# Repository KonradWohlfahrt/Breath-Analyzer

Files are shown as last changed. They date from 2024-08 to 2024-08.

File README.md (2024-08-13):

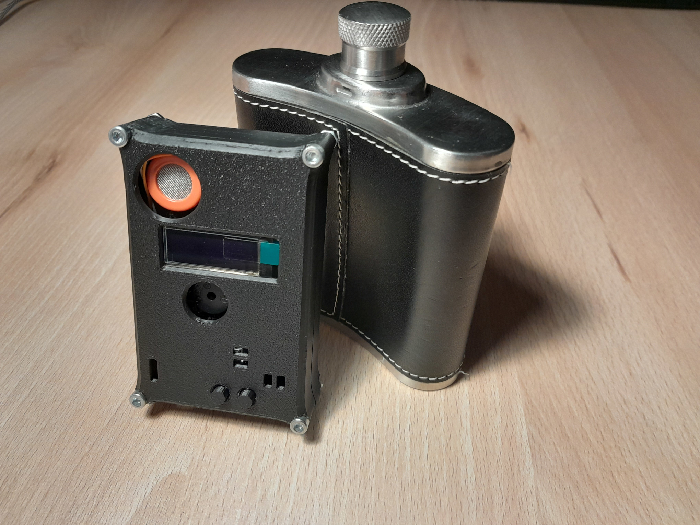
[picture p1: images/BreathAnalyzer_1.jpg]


# DIY BREATH ANALYZER
In this repository you'll find the files for my DIY Breath Analyzer based on the MQ3 Sensor.
Check out my step-by-step guide on [Instructables](https://www.instructables.com/DIY-Breath-Analyzer-With-the-MQ3/).<br>
**NOTE:** This device may not have good accuracy and should not be used as a way to determine your blood alcohol concentration. Refer to commercial products instead! Furthermore, this project was sponsored by [PCBWay](https://www.pcbway.com/). They were so kind to produce the circuit board for this project. PCBWay offers different services, such as pcb fabrication. 
It was the first time for me to use their service. With the gerber files the process of ordering was simple and fast. The quality of the pcbs is awesome! Prefect to bring your diy project to the next level!
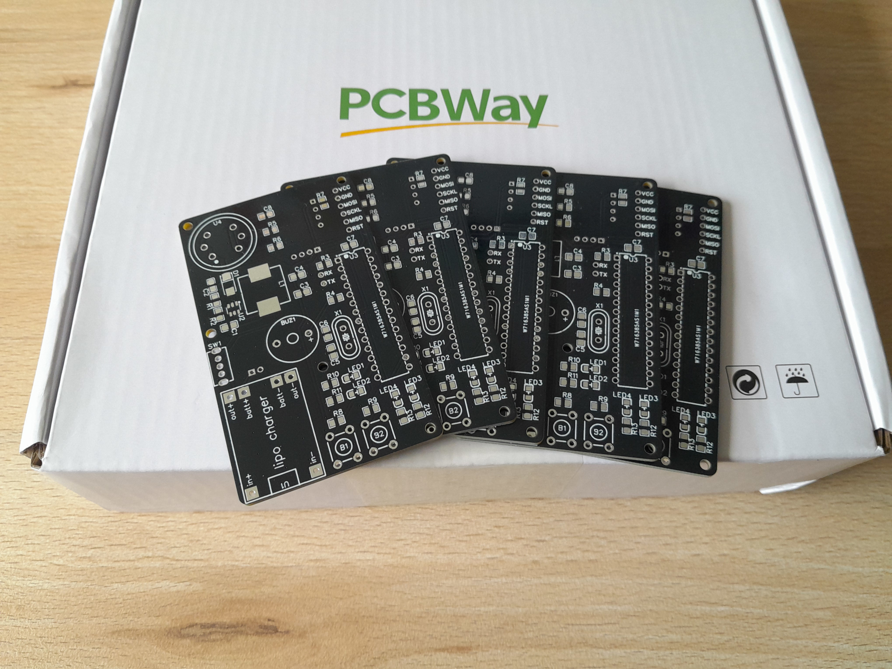
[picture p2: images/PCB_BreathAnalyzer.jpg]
PCBs


***
# BUILDING

**Materials:**<br>
| Component | Amount | Silkscreen label |
|:----------|:------:|-----------------:|
| custom pcb | 1 | - |
| 3D printed case | 1 | - |
| 0.91 I2C OLED display | 1 | - |
| lipo battery | 1 | U6 |
| 2 Pin PH2.0 socket (optional) | 1 | U6 |
| TP4056 charging module | 1 | U1 |
| MT3608 | 1 | U2 |
| ATmega328P + socket (optional) | 1 | U3 |
| MQ3 | 1 | U4 |
| DHT11 | 1 | U5 |
| 16 MHz crystal oscillator | 1 | X1 |
| Piezo buzzer | 1 | BUZ1 |
| Push button 6x6 | 2 | B1,B2 |
| SK12D07VG6 | 1 | SW1 |
| 22uH | 1 | L1 |
| SS34 | 1 | D1 |
| LED 0805 red | 2 | LED1,LED4 |
| LED 0805 green | 1 | LED3 |
| LED 0805 (free color choice) | 1 | LED2 |
| 22uF 0805 | 2 | C1,C2 |
| 10uF 0805 | 1 | C3 |
| 1uF 0805 | 1 | C4 |
| 22pF 0805 | 2 | C5,C6 |
| 100nF 0805 | 2 | C7,C8 |
| 220k 0805 | 1 | R1 |
| 30k 0805 | 1 | R2 |
| 10k 0805 | 4 | R3,R7-R9 |
| 220r 0805 (optional, connect with solder instead) | 1 | R4 |
| 5.1r or 10r 0805 | 1 | R5 |
| 4.7k 0805 | 1 | R6 |
| 1k 0805 | 4 | R10-R13 |
| M2.5x12mm screw + nut | 4 | - |
| M3x20mm screw + nut | 4 | - |

**Soldering:**<br>
Begin to solder the boost converter (U2,D1,L1,C1,C2,R1,R2) and confirm the output voltage of roughly 5V.
Now you can proceed to solder the smd components first and through-hole components second.
You may want to [change](https://www.youtube.com/watch?v=6asCEBm4ZAw) the charge programming resistor of the TP4056 module. Add pins to VCC,GND,MOSI,SCKL,MISO,RST to flash the ATmega. You do not need pins on rx and tx.
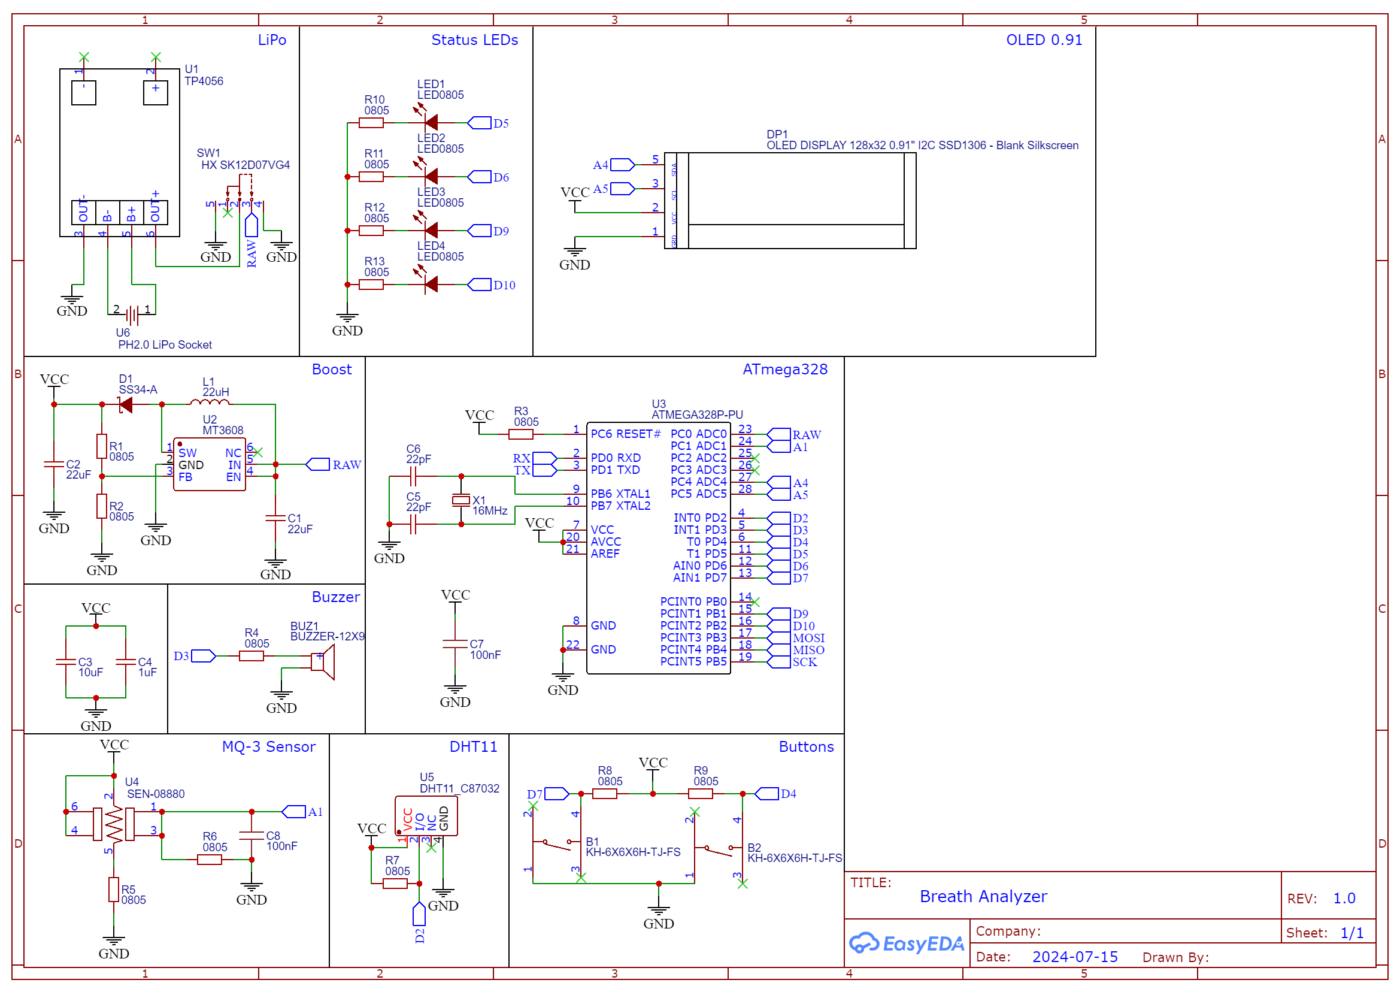
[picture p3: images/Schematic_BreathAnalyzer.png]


***
# Programming and Testing
Heating the sensor once for (over) 24 hours is sufficient to get stable readings. If you leave the device powered off for too long, you should repeat this step.
Install the `MiniCore` board manager, `U8g2`, `DHT` library and upload the test code via an Arduino Uno with `Arduino As ISP`.  Press the buttons to toggle between values: analog value; voltage; sensor resistance; bac in per mille (note: calculate r0 for your sensor first); temperature and humidity.
Flash `BreathAnalyzer.ino` on the Atmega if everything worked as expected and unplug all cables. After plugging in the battery and turning on the device, it should heat up for 30 seconds. Navigate to settings and start to calibrate the device (expose the sensor to clean air only). 
Print the case with the two buttons and screw everything in place. Now your DIY Breath Analyzer is all set up!
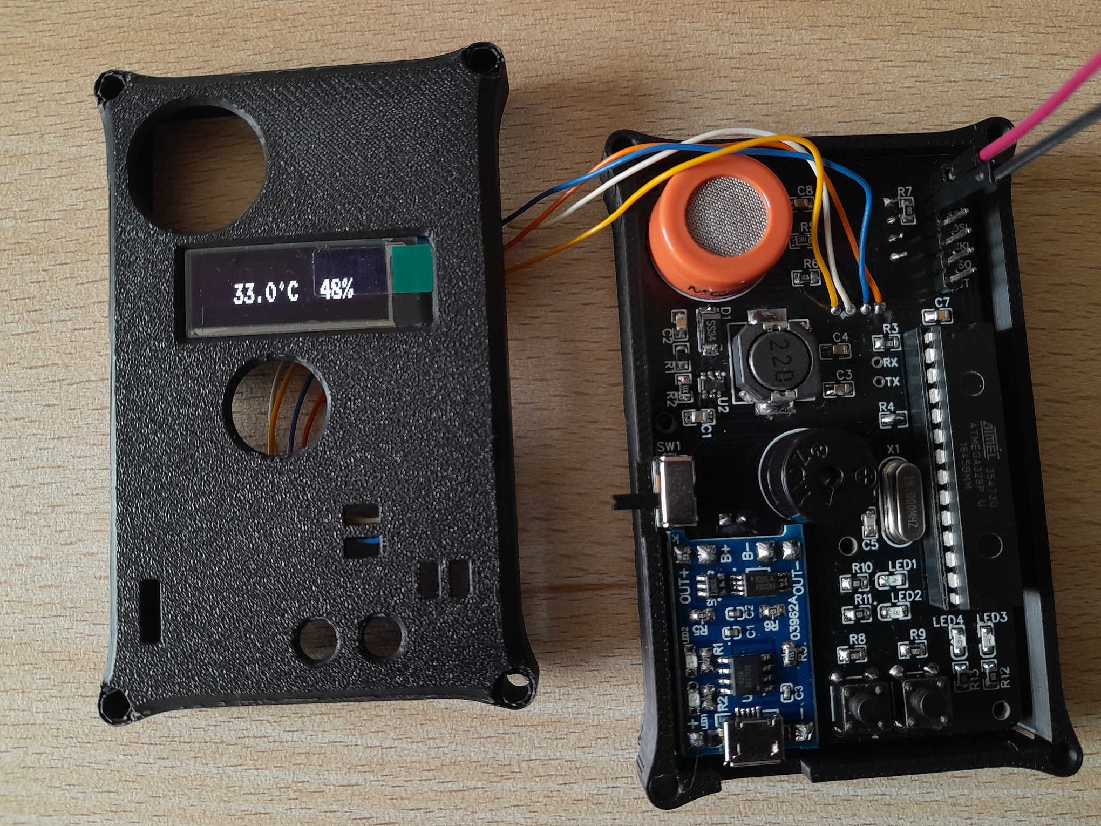
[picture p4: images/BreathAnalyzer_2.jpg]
Testing


***
# Navigation
- sleep mode: press any button to wake up the device
- idle mode: press any button to measure your bac in per mille
- idle mode: press both buttons to enter settings mode
- settings mode: toggle between settings with mode button (left) and change with set button (right)
- settings mode: press both buttons to leave settings mode and save values to eeprom
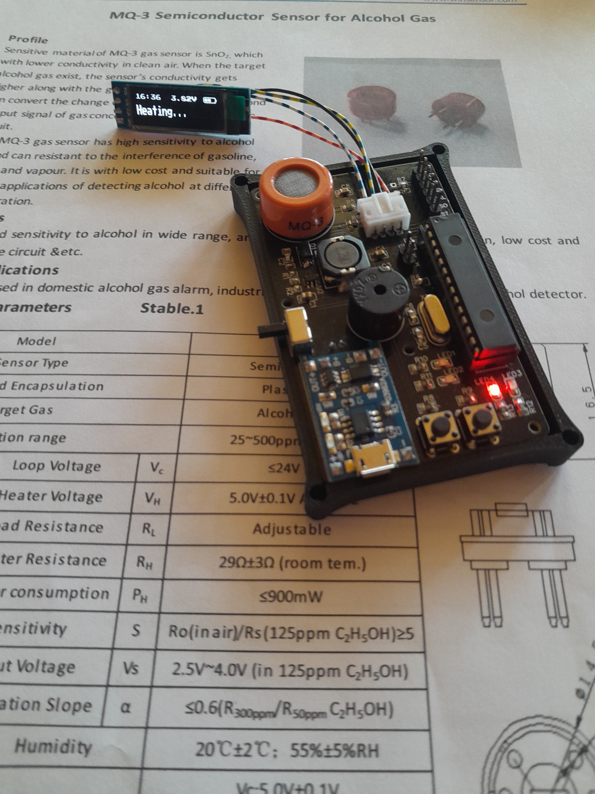
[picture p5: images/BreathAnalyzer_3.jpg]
Calibrate


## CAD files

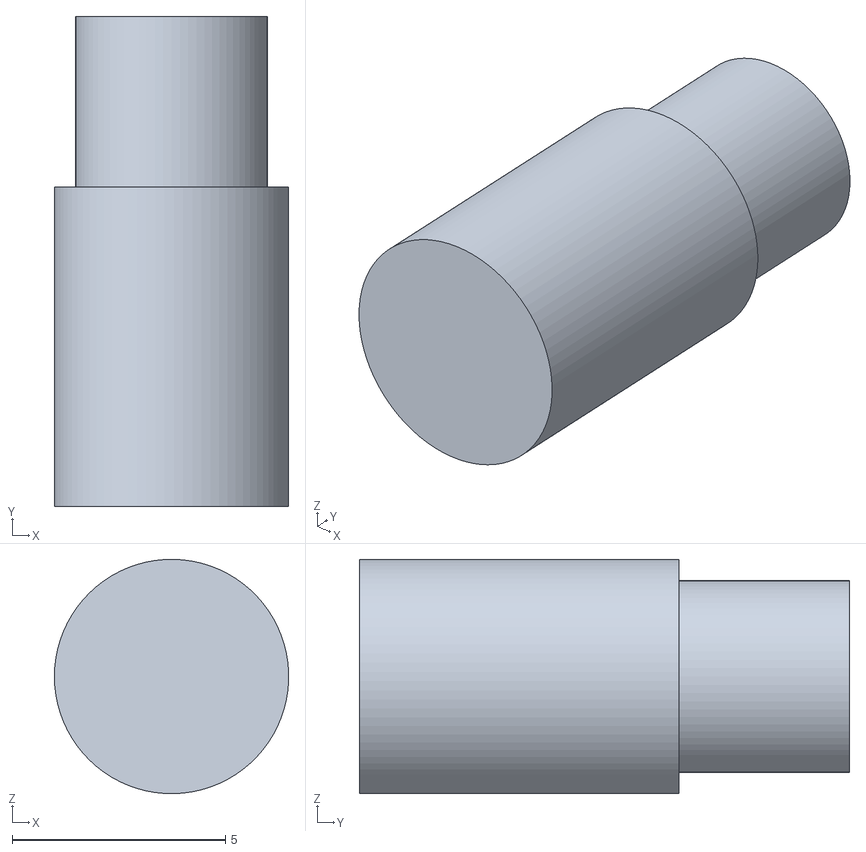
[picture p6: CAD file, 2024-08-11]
cad/Button.stl
5.50 x 11.5 x 5.50

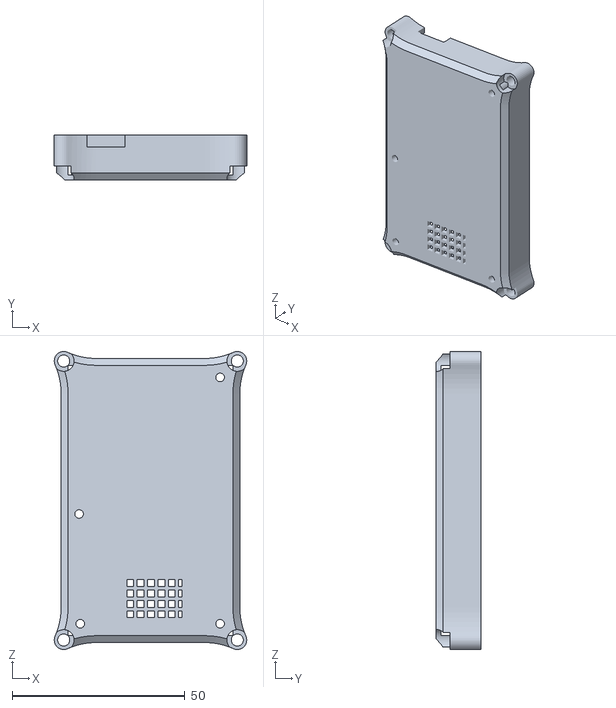
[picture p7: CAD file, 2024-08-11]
cad/CaseBottom.stl
55.7 x 13.0 x 86.2

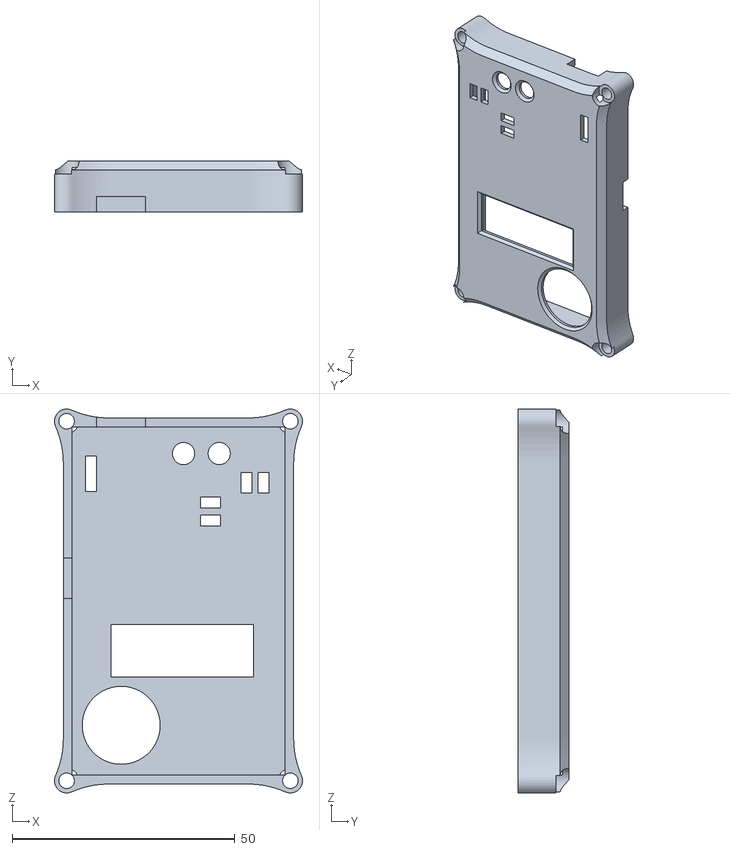
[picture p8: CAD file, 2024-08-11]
cad/CaseTop.stl
55.7 x 11.5 x 86.2

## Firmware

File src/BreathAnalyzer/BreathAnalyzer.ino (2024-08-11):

#include <U8x8lib.h>
#include <DHT.h>
#include <EEPROM.h>

#define DHTPIN 2
#define DHTTYPE DHT11

#define BATPIN A0
#define SENSOR A1

#define LEFTBUTTON 4
#define RIGHTBUTTON 7

#define BUZZER 3
#define BUZZERVOLUME 127
#define BUZZERTIME 15

#define LOWBATLED 5
#define SLEEPLED 6
#define GREENLED 9
#define REDLED 10


// enter your output voltage here or leave at 5V
#define VOLTS 5.0f
// leave if VOLTS=5.0f, or calculate by: (3.9V, 3.7V, 3.6V, 3.55V) / VOLTS * 1023s
#define FULLCHARGE 798
#define NORMALCHARGE 757
#define LOWCHARGE 737
#define EMPTYCHARGE 726

// enter your load resistor here if changed
#define R6 4700
// clean air factor from datasheet: rs/r0 in clean air is 60
#define CLEANAIRFACTOR 60.0f


// gas concentration graph, values from datasheet
// P1(50ppm, 0.17 Rs/R0) 
// P2(500ppm, 0.0225 Rs/R0)
const float point1[] = { log10(50), log10(0.17) };
const float point2[] = { log10(500), log10(0.0225) };
const float scope = (point2[1] - point1[1]) / (point2[0] - point1[0]);
const float coord = point1[1] - point1[0] * scope;

// display tiles
const uint8_t batteryBackground[24] = { 0x00, 0x00, 0x7e, 0x81, 0x81, 0x81, 0x81, 0x81,
  0x81, 0x81, 0x81, 0x81, 0x81, 0x81, 0x81, 0x81,
  0x81, 0x81, 0x81, 0xc3, 0x7e, 0x18, 0x00, 0x00 };
const uint8_t oneBatteryBar[8] = { 0x00, 0x00, 0x7e, 0x81, 0xbd, 0xbd, 0xbd, 0xbd };
const uint8_t twoBatteryBars[8] = { 0x81, 0xbd, 0xbd, 0xbd, 0xbd, 0x81, 0x81, 0x81 };
const uint8_t threeBatteryBars[16] = { 0x81, 0xbd, 0xbd, 0xbd, 0xbd, 0x81, 0xbd, 0xbd, 0xbd, 0xbd, 0x81, 0xc3, 0x7e, 0x18, 0x00, 0x00 };
const uint8_t arrowUpperTile[8] = { 0xfc, 0xf8, 0xf0, 0xe0, 0xc0, 0x80, 0x00, 0x00 };
const uint8_t arrowLowerTile[8] = { 0x3f, 0x1f, 0x0f, 0x07, 0x03, 0x01, 0x00, 0x00 };

// text
const char* loadingTxt = "Loading...";
const char* soundTxt = "Sound";
const char* contrastTxt = "Contrast";
const char* calibrateTxt = "Calibrate";
const char* calculateTxt = "Calculating...";
const char* heatingTxt = "Heating...";
const char* blowTxt = "Blow...";
const char* bacTxt = "BAC: ";
const char* onTxt = "on";
const char* offTxt = "off";


U8X8_SSD1306_128X32_UNIVISION_HW_I2C u8x8(U8X8_PIN_NONE);
DHT dht(DHTPIN, DHTTYPE);

bool sleeping = false;
unsigned long interactionTimestamp;
unsigned long tempCheckTimestamp;
unsigned long batteryCheckTimestamp;

unsigned int R0;

uint8_t settingsIndex = 0;
uint8_t contrast;
bool buzzerActive;


bool modeButton() { return digitalRead(LEFTBUTTON) == 0; }
bool setButton() { return digitalRead(RIGHTBUTTON) == 0; }
bool anyButton() { return modeButton() || setButton(); }
bool allButtons() { return modeButton() && setButton(); }

float analogToVolt(int value) { return (float)value / 1023.0f * VOLTS; }
float getSensorResistance(int adc) { return ((float)R6 * (1023.0f - adc) / adc); }
float getConcentration(float resistance) { return pow(10, coord + scope * log(resistance / R0)); }

bool isTimestamp(unsigned long& timestamp, int interval) 
{
  if (millis() - timestamp >= interval)
  {
    timestamp = millis();
    return true;
  }
  return false;
}
void setBuzzerIgnore(int time)
{
  analogWrite(BUZZER, BUZZERVOLUME);
  delay(time);
  analogWrite(BUZZER, 0);
}
void setBuzzer(int time)
{
  if (!buzzerActive)
    return;
  setBuzzerIgnore(time);
}
void setBuzzer() { setBuzzer(BUZZERTIME, false); }


void setup() 
{
  // initialize pins
  pinMode(BATPIN, INPUT);
  pinMode(SENSOR, INPUT);
  pinMode(LEFTBUTTON, INPUT);
  pinMode(RIGHTBUTTON, INPUT);

  pinMode(BUZZER, OUTPUT);
  pinMode(LOWBATLED, OUTPUT);
  pinMode(SLEEPLED, OUTPUT);
  pinMode(GREENLED, OUTPUT);
  pinMode(REDLED, OUTPUT);

  // initialize display, dht11 sensor
  u8x8.begin();
  u8x8.setFont(u8x8_font_pressstart2p_f);
  u8x8.draw1x2String(0, 2, loadingTxt);
  dht.begin();
  
  // read settings from eeprom
  EEPROM.begin(); // 2 bytes (R0), 1 byte (contrast), 1 byte (sound)
  delay(250);
  EEPROM.get(0, R0);
  contrast = EEPROM.read(2);
  buzzerActive = EEPROM.read(3) == 1;

  u8x8.setContrast(contrast);

  setBuzzer();
  heating(30000); // heat for 30 seconds to get stable readings

  showStartScreen();
  interactionTimestamp = millis();
}
void loop() 
{
  if (sleeping)
  {
    checkBattery(false);
    if (anyButton())
    {
      analogWrite(SLEEPLED, 0);
      while (anyButton());
      sleeping = false;
      interactionTimestamp = millis();
      showStartScreen();
      u8x8.setPowerSave(0);
    }
    return;
  }
  // sleep after 5s
  else if (isTimestamp(interactionTimestamp, 5000)) 
  {
    sleeping = true;
    u8x8.setPowerSave(1);
    analogWrite(SLEEPLED, 127);
    return;
  }

  // handle input
  if (anyButton())
  {
    bool both = false;
    while (anyButton())
    {
      checkBattery(false);
      displayTemp(false);
      if (!both && allButtons())
        both = true;
    }

    if (!both)
      measure();
    else
      settings();

    showStartScreen();
    interactionTimestamp = millis();
  }

  checkBattery(false);
  displayTemp(false);
}

void settings()
{
  setBuzzer();
  settingsIndex = 0;
  u8x8.clearDisplay();
  checkBattery(true);
  showSettings();

  while (true)
  {
    checkBattery(false);
    if (anyButton())
    {
      bool set = setButton();
      bool both = false;
      while (anyButton())
      {
        checkBattery(false);
        if (!both && allButtons())
          both = true;
      }
      
      if (both)
        break;
      else
      {
        if (set)
        {
          if (settingsIndex == 0)
          {
            buzzerActive = !buzzerActive;
            setBuzzer();
          }
          else if (settingsIndex == 1)
          {
            if (contrast == 0)
              contrast = 50;
            else if (contrast == 50)
              contrast = 127;
            else if (contrast == 127)
              contrast = 255;
            else
              contrast = 0;
            u8x8.setContrast(contrast);
            setBuzzer();
          }
          else
            calibrate();
        }
        else
        {
          settingsIndex++;
          if (settingsIndex > 2)
            settingsIndex = 0;
          setBuzzer();
        }

        showSettings();
      }
    }
  }

  setBuzzer();

  EEPROM.update(2, contrast);
  EEPROM.update(3, buzzerActive);
}
void calibrate()
{
  setBuzzer();
  heating(600000); // heat for 10 minutes

  setBuzzer(BUZZERTIME * 2);
  delay(BUZZERTIME * 2);
  setBuzzer(BUZZERTIME * 2);

  u8x8.clearDisplay();
  u8x8.draw1x2String(0, 2, calculateTxt);

  // get average of 50 analog reads
  unsigned int avg = 0;
  for (uint8_t i = 0; i < 50; i++)
  {
    avg += analogRead(SENSOR);
    delay(200);
  }
  avg /= 50;

  R0 = (unsigned int)(getSensorResistance(avg) / CLEANAIRFACTOR); // divide by clean air factor (datasheet) to get r0

  u8x8.clearDisplay();
  u8x8.drawString(0, 1, (String(avg) + " - " + String(analogToVolt(avg), 2) + "V").c_str());
  u8x8.drawString(0, 2, ("R0: " + String(R0)).c_str());

  EEPROM.put(0, R0);

  delay(5000);
}
void measure()
{
  // heat
  setBuzzer();
  heating(5000);
  
  // blow
  setBuzzer();
  int reading = getBlowSamples();

  // calculate bac
  // ppm * 0.9988590004 = mg/l
  // mg/l * 2 = per mille
  float bac = getConcentration(getSensorResistance(reading)) * 1.997718f;

  // display bac
  u8x8.clearDisplay();
  u8x8.draw1x2String(0, 2, (bacTxt + String(bac, 3)).c_str());
  checkBattery(true);
  
  if (bac >= 0.5f)
  {
    analogWrite(REDLED, 255);
    setBuzzer(BUZZERTIME * 2);
  }
  else 
  {
    analogWrite(GREENLED, 255);
    setBuzzer();
  }
    
  delay(5000);
  analogWrite(REDLED, 0);
  analogWrite(GREENLED, 0);
}


void heating(unsigned long time)
{
  u8x8.clearDisplay();
  u8x8.draw1x2String(0, 2, heatingTxt);
  checkBattery(true);

  uint8_t v = 0;
  bool up = true;

  unsigned long start = millis();
  int lastSec = 0;
  while (millis() - start < time)
  {
    unsigned long remaining = time - (millis() - start);
    int seconds = remaining / 1000 % 60;

    if (lastSec != seconds)
    {
      lastSec = seconds;
      int minutes = remaining / 1000 / 60;
      u8x8.drawString(0, 0, ((minutes < 10 ? "0" + String(minutes) : String(minutes)) + ":" + (seconds < 10 ? "0" + String(seconds) : String(seconds))).c_str());
    }

    checkBattery(false);

    if (up)
      v++;
    else
      v--;
    if (v == 255 || v == 0)
      up = !up;
    
    analogWrite(REDLED, v);
    delay(2);
  }
  analogWrite(REDLED, 0);
}
int getBlowSamples()
{
  u8x8.clearDisplay();
  u8x8.draw1x2String(0, 2, blowTxt);
  checkBattery(true);

  analogWrite(GREENLED, 255);

  unsigned int avg = 0;
  int amount = 0;
  unsigned long start = millis();
  while (millis() - start < 4500)
  {
    unsigned long remaining = 4500 - (millis() - start);
    u8x8.draw1x2String(13, 2, ("0" + String(remaining / 1000)).c_str());

    if (remaining <= 1500)
    {
      avg += analogRead(SENSOR);
      amount++;
      
      delay(20);
    }

    checkBattery(false);
  }
  analogWrite(GREENLED, 0);
  avg /= amount;
  return avg;
}


void showStartScreen()
{
  u8x8.clearDisplay();
  checkBattery(true);
  displayTemp(true);
}
void showSettings()
{
  u8x8.clearLine(1);
  u8x8.clearLine(2);
  u8x8.clearLine(3);

  u8x8.drawTile(0, 2, 1, arrowUpperTile);
  u8x8.drawTile(0, 3, 1, arrowLowerTile);
  switch (settingsIndex)
  {
    case 0:
      u8x8.draw1x2String(1, 2, soundTxt);
      if (buzzerActive)
        u8x8.draw1x2String(13, 2, onTxt);
      else
        u8x8.draw1x2String(12, 2, offTxt);
      break;
    case 1:
      u8x8.draw1x2String(1, 2, contrastTxt);
      if (contrast < 100)
        u8x8.draw1x2String(13, 2, String(contrast).c_str());
      else
        u8x8.draw1x2String(13, 2, String(contrast).c_str());
      break;
    case 2:
      u8x8.draw1x2String(1, 2, calibrateTxt);
      u8x8.drawString(0, 1, ("R0: " + String(R0)).c_str());
      break;
  }
}


void checkBattery(bool force)
{
  if (!force && !isTimestamp(batteryCheckTimestamp, 2000))
    return;

  unsigned int avg = 0;
  for (uint8_t b = 0; b < 15; b++)
  {
    avg += analogRead(BATPIN);
    delay(5);
  }
  avg = avg / 15;

  if (avg >= FULLCHARGE)
  {
    displayBattery(3);
  }
  else if (avg >= NORMALCHARGE)
  {
    displayBattery(2);
  }
  else if (avg >= LOWCHARGE)
  {
    displayBattery(1);
  }
  else if (avg >= EMPTYCHARGE)
  {
    displayBattery(0);
    analogWrite(LOWBATLED, 128);
  }
  else
  {
    setBuzzerIgnore(BUZZERTIME * 2);delay(BUZZERTIME * 2);setBuzzerIgnore(BUZZERTIME * 2);
    analogWrite(SLEEPLED, 0);
    analogWrite(GREENLED, 0);
    analogWrite(REDLED, 0);
    analogWrite(BUZZER, 0);
    u8x8.setPowerSave(1);
    while (true) 
    {
      analogWrite(LOWBATLED, 32);
      delay(500);
      analogWrite(LOWBATLED, 0);
      delay(1500);
    }
  }

  if (!sleeping)
    u8x8.drawString(7, 0, (String(analogToVolt(avg), 2) + "V").c_str());
}
void displayBattery(uint8_t i)
{
  if (sleeping)
    return;
  u8x8.drawTile(13, 0, 3, batteryBackground);
  if (i != 0)
    u8x8.drawTile(13, 0, 1, oneBatteryBar);
  if (i == 2)
    u8x8.drawTile(14, 0, 1, twoBatteryBars);
  else if (i == 3)
    u8x8.drawTile(14, 0, 2, threeBatteryBars);
}
void displayTemp(bool force)
{
  if (sleeping)
    return;
  if (!force && !isTimestamp(tempCheckTimestamp, 2000))
    return;

  String t = String(dht.readTemperature(), 1);
  String h = String((int)dht.readHumidity());

  char txt[12] = { t[0], t[1], '.', t[3], '°', 'C', ' ', ' ', h[0], h[1], '%', '\0' };
  if (h.length() >= 3)
  {
    txt[7] = h[0];
    txt[8] = h[1];
    txt[9] = h[2];
  }
  
  u8x8.draw1x2String(3, 2, txt);
}

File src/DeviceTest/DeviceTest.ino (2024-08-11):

#include <U8x8lib.h>
#include <DHT.h>
#include <EEPROM.h>

#define DHTPIN 2
#define DHTTYPE DHT11

#define SENSOR A1

#define LEFTBUTTON 4
#define RIGHTBUTTON 7


// enter your output voltage here or leave at 5V
#define VOLTS 5.0f

// enter your resistor here if changed
#define R6 4700
// R0 = sensor resistance (in clean air) / 60.0f
#define R0 267

// gas concentration graph
const float point1[] = { log10(50), log10(0.17) };
const float point2[] = { log10(500), log10(0.0225) };
const float scope = (point2[1] - point1[1]) / (point2[0] - point1[0]);
const float coord = point1[1] - point1[0] * scope;


U8X8_SSD1306_128X32_UNIVISION_HW_I2C u8x8(U8X8_PIN_NONE);
DHT dht(DHTPIN, DHTTYPE);


int index = 0;
unsigned long timestp;


bool modeButton() { return digitalRead(LEFTBUTTON) == 0; }
bool setButton() { return digitalRead(RIGHTBUTTON) == 0; }
bool anyButton() { return modeButton() || setButton(); }

float getSensorResistance(int adc) { return ( ((float)R6 * (1023.0f - adc) / adc)); }
float getConcentration(float resistance) { return pow(10, coord + scope * log(resistance / R0)); }
float analogToVolt(int value) { return (float)value / 1023.0f * VOLTS; }

bool isTimestamp(unsigned long& timestamp, int interval) 
{
  if (millis() - timestamp >= interval)
  {
    timestamp = millis();
    return true;
  }
  return false;
}


void setup() 
{
  // initialize pins
  pinMode(SENSOR, INPUT);
  pinMode(LEFTBUTTON, INPUT);
  pinMode(RIGHTBUTTON, INPUT);

  // initialize display, dht11 sensor
  u8x8.begin();
  u8x8.setFont(u8x8_font_pressstart2p_f);
  dht.begin();
}
void loop() 
{
  if (anyButton()) {
    while (anyButton());
    index = (index + 1) % 5;
    updateDisplay();
    timestp = millis();
  }

  if (isTimestamp(timestp, 500))
    updateDisplay();
}

void updateDisplay()
{
  u8x8.clearLine(2);
  u8x8.clearLine(3);

  unsigned int avg = 0;
  for (uint8_t i = 0; i < 50; i++)
  {
    avg += analogRead(SENSOR);
    delay(2);
  }
  avg /= 50;

  if (index == 0)
  {
    u8x8.draw1x2String(0, 2, String(avg).c_str());
  }
  else if (index == 1)
  {
    float sensorVolt = analogToVolt(avg);
    u8x8.draw1x2String(0, 2, (String(sensorVolt, 2) + "V").c_str());
  }
  else if (index == 2)
  {
    unsigned int r = getSensorResistance(avg);
    u8x8.draw1x2String(0, 2, String(r).c_str());
  }
  else if (index == 3)
  {
    float bac = getConcentration(getSensorResistance(avg)) * 1.997718f; // ppm to per mille
    u8x8.draw1x2String(0, 2, String(bac, 3).c_str());
  }
  else
  {
    String t = String(dht.readTemperature(), 1);
    String h = String((int)dht.readHumidity());

    char txt[12] = { t[0], t[1], '.', t[3], '°', 'C', ' ', ' ', h[0], h[1], '%', '\0' };
    if (h.length() >= 3)
    {
      txt[7] = h[0];
      txt[8] = h[1];
      txt[9] = h[2];
    }
    
    u8x8.draw1x2String(3, 2, txt);
  }
}
